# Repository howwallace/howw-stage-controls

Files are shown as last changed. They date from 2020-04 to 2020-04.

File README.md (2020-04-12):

# howw-stage-controls

AUTHOR:		Harper O. W. Wallace  
DATE:		12 Apr 2020

#### DESCRIPTION OF STAGES SETUP:

This library executes move commands for Zaber Technologies rotary (1 x X-RSW60A) and linear (2 x T-LSM050A) stages, all using binary encoding, and it supervises voltage and current control of Keithley 2400 SourceMeter to open and close a Thorlabs SH05 beam shutter.

The two linear stages are mounted in the plane of the ground (one atop the other) and oriented orthogonally such that, from the perspective of the upper stage's platform, one stage controls the "x-coordinate of position," and the other controls the "y-coordinate." Film samples prepared on 1-inch microscope slides can be mounted on the upper stage using a 3D-printed slide-holder (slide_holder.stl) that I designed to be compatible with Zaber T-LSM050A stages.

The upper stage's platform has a range of motion such that the laser beam emitted from a 671nm, 450mW Laserglow laser module can strike any point in much of the central area of the upper platform, and therefore any point on a mounted film sample. The beam is projected horizontally above the stages, strikes a mirror and reflects vertically down, and is focused through a 10x microscope objective; it can be interrupted programmatically by means of a Thorlabs SH05 beam shutter (mounted between source and mirror), which is operated by modulating current from the Keithley 2400 SourceMeter (cf. keithley_handler.py). The 10x microscope objective is suspended in the beam path (vertically; after reflection) and above the film sample, in the optic holder of a modified student microscope whose coarse control is connected to the rotary stage to allow for programmatic control of the distance between lens and sample (corresponds to "z" in execute_commands.py).

"Writing" (used below and in .py files) entails moving a thin film of thermoresponsive materials (donor-acceptor columnar liquid crystals) on the stages beneath the focused beam to control their columnar alignment. For this particular application, particular considerations must be made to speed, power, and focal distance, but for the purposes of this overview, it is sufficient to say that the path that the beam follows corresponds to the pattern written to the sample.

___

#### execute_commands.py:

Parametrized move commands allow the user to write a single line, write parallel lines, write part of a circle, write a full circle, wipe a region, outline a region, and home all stages merely by specifying relevant parameters (e.g., circle center, radius, and write speed); many of these write functions are parametrized in several different ways in order to simplify writing slight variations on the same type of pattern (e.g., horizontal lines that span the entire sample region, v. vertical lines that span a specified sub-region, v. diagonal lines that are separated by a specified perpendicular distance). These commands and their arguments are detailed in execute_commands.py.

#### coordinates.py:

A Cartesian coordinate system keeps track of sample boundaries and write command positions within them. This system confers particular advantages in allowing the user to keep track of previously-written and new patterns in a systematic way, and also in conserving area on sample films in order to maximize their usefulness between wipes.

The coordinate system is defined by two critical parameters (1–2) and one very helpful one (3):
1. **GLOBAL_O** (*V2*) = "global origin," or the x- and y- stage positions when the laser beam is focused on the bottom-left corner of a square sample film
2. **TR** (*V2*) = "top right," etc.
3. **LOCAL_O** (*V2*) = "local origin," effectively a pointer vector from the origin, which allows the coordinate system to be sub-defined for a given write command, without needing to redefine GLOBAL_O or TR.

Although GLOBAL_O stands for "global origin," TR is actually another global origin and is often the more critical of the two to determine accurately, since it is ends up defining the apparent "bottom left" origin position relative to which moves are made, once the coordinate system is inverted to account for inversion on viewing under a microscope.

The user can define values for GLOBAL_O and TR using POSITION_GETTER_MODE (in execute_commands.py), which allows her to take manual control of the stages (using control knobs on the stages themselves) to adjust their position until they reach a desired position on the sample (e.g., GLOBAL_O or TR). At this point, the user can press the 'p' key on the keyboard to print the position of the stages to the console, so they may be recorded, e.g., to define GLOBAL_O and TR for a new sample (press 'esc' once these values have been recorded).

Units are millimeters, but neither class of Zaber stages uses this unit explicitly; instead, they use microsteps (which I call "data" in conversion methods, because those values are what ends up getting sent to the devices). Conversion factors between distance and speed are not intuitive, and they are different for the rotary and linear stages. Understanding how these units are interconverted is key to resolving issues where the stages do not behave as expected, which can happen. Consult [1] for a detailed explanation of Zaber's units and conversions.

This coordinate system will be more useful if it is specified for EACH film sample. To facilitate maintaining these boundary positions for different samples, I have designed (and installed, in our setup in Ebaugh Labs at Denison University) a 3D-printable 1-inch glass microscope slide holder that can be mounted to the Zaber T-LSM050A stage so that this coordinate system is approximately (~0.01mm) conserved on removal and replacement of the sample (cf. slide_holder.stl). Values for GLOBAL_O and TR should be stored in sample-specific .txt files (cf. samples/_example.txt), which are read by execute_commands.py 

#### mapping_handler.py

A new and experimental feature of this library is move mapping, which theoretically allows the user to simulate how write commands will turn out in order to correct any errors before running them on a sample; as a sort of extension of the coordinate system itself, this feature too is meant to help conserve space on the film and maximize usefulness between writes. Move mapping will be particularly advantageous for writing multi-step patterns that will be necessary to generate complex diffraction gratings for Fourier projection and holographic images. As I explain in more detail in the header of mapping_handler.py, rendering hasn't been rigorously tested yet; but it verifying predicted paths for different commands should be straightforward, and a procedure is outlined in the header of mapping_handler.py.

mapping_handler.py consults the .txt data file corresponding to the relevant film sample to gather historical write data and defined global origins. These film sample files must be made available for each sample (at the path specified in execute_commands.py), and in the format specified in samples/_example.txt and samples/_template.txt. Notes on how film sample files are used are offered in execute_commands.py, but here are some notes on syntax:
- Film sample files are interpreted in such a way that is compatible with the actual Python syntax for calling these commands. This allows the user to copy and paste commands between sample .txt files and the manual command-calling section of execute_commands.py (rather than having to reformat from some other input format). It makes using Move Mapping much more convenient (if only because you have to be familiar with only one command-calling syntax), but you should note that parsing out varied-type (e.g., int, float, V2, arrays) arguments from a string in a text file is nontrivial: it is critical that you use exactly the format that I describe in samples/_template.txt, and even so it is also possible that there are some text-parsing bugs that you will need to resolve.
- The interpreter will respect Python-syntax line comments (i.e., "# ..."), so I'd recommend commenting in information about laser power so you can keep track of it.
- Film sample data files use a special symbol ("## ...") to mark section divisions between already-written commands, new commands, and references; this symbol should not appear elsewhere than those three places (cf. samples/_template.txt).

Limitations of mapping_handler.py:
- If you want to modify a command method (e.g., write_line(...)), then you'll have to make sure that the corresponding section in mapping_handler.py is updated; if you want to add a new command method, then you'll need to define one in mapping_handler.py for it to be rendered.
- It assumes that your frame of reference for writing is based on the image on viewing under a microscope, which is an inversion of how patterns are actually written to the sample (i.e., assumes INVERT = True, cf. execute_commands.py). This means that if you change the value of INVERT in execute_commands.py, then the preview rendered by mapping_handler.py will be inverted.
- It hasn't been designed to shift shift historical information if you redefine a sample's GLOBAL_O or TR.

___

#### EXTREMELY IMPORTANT NOTES:
1. **DO NOT LET THE OBJECTIVE LENS HIT THE SAMPLE HOLDER SCREWS:**
Although it is possible to programmatically set a minimum height for the rotary stage to alleviate concerns like this, unfortunately the screws are sufficiently elevated above the sample that the focal distance would probably be too large to write at modest power, if you were to try that (rather than doing it that way, I have set the minimum position such that the aluminum jacket for the objective lens will not collide with the screws, so that the linear stages should not be damaged in a collision). Therefore it is EXTREMELY IMPORTANT that you move the stages such that the objective lens is someplace within the sample region, THEN lower the objective lens to the correct focal distance. This is done automatically in the parametrized move commands defined below, but if you define any more, or if you call move_to(...), then you must consider stage height.

2. **DO NOT MELT THE BEAM SHUTTER BY LEAVING THE LASER BEAM ON IT TOO LONG:**
If the laser spot is on the shutter leaves for too long, they will deform and the diaphragm will no longer be able to open and close. For the ThorLabs SH05 beam shutter we are using, about ten seconds is safe given the wavelength, spot size, and highest throughput of our laser (according to a ThorLabs Application Technician). This can be an inconvenience when you would like to move around the sample film without dragging an isotropic line behind you, e.g., and so it means that you may have to find creative ways to organize writing to minimize the time that the laser needs to be effectively "off"; alternatively, you may find that raising the objective lens sufficiently high will diffuse the beam such that you can move the sample without aligning/disaligning; as a last resort, you may need to TURN THE LASER OFF MANUALLY in certain circumstances, rather than relying on the beam shutter.

3. **DO NOT MOVE THE ROTARY STAGE AT TOO GREAT A SPEED OR ACCELERATION:**
Stage accelerations are defined in execute_commands.py (define_operating_constants), and I strongly recommend that you not alter them. The primary reason that you should not increase the rotary stage acceleration is that it'd be a huge problem if you bent or snapped the pin that runs through the coarse control of the microscope stage and which the rotary stage is rotating to control stage height; if this pin twists too abruptly (and I have no idea what the damage threshold is), you're probably going to need to build a new z-control stage and a new control adapter for the rotary stage, and you may do direct damage to the rotary stage and/or the object lens.
It's also important not to let the rotary stage move too fast: though it is possible with the linear stages, incorrect moves of the rotary stage are much more likely to cause actual damage (to the objective lens, to the sample, to the linear stages, and to itself). I've set an upper bound on speed so that the rotary stage moves slowly; this allows you to manually stop it (by pressing in once on the manual control knob) if it looks like it's heading for dangerous territory.

4. **YOU CAN INTERRUPT PROGRAMMED STAGE MOVES BY PRESSING SHIFT-CTRL-C**
I strongly recommend playing around with sending commands and interrupting them with Shift-Ctrl-C so you know. One notable quirk is that, if you interrupt writing a circle, the most recent move_vel command stands, and so one or both of the linear stages may just keep going until it is fully extended; obviously, this is a big concern if the tip of the objective lens is below the level of the sample holder screws.

5. **PUTTING A Nd MAGNET ARRAY DIRECTLY ON THE LINEAR STAGES INTERFERES WITH THEIR OPERATION**
They sort of spazzed out there, for a while. If you are interested in aligning in a strong B field, then make sure that you have the magnet array sufficiently far away from the stages (e.g., mounted above, with a several-inch spacer).

#### TROUBLESHOOTING:
- In Zaber Console, if pressing the "Stop" button does not update a stage's current position, it's probably because disable_auto_reply (used in binarydevice.py to selectively silence/allow responses) is still on. Still in Console, click on the device, then Settings, and reset "Device Mode" such that bit 0 = 0 (i.e., round down to the nearest even number).
- ModuleNotFoundError probably means that it has not been installed. Instructions for installing pip: https://pip.pypa.io/en/stable/installing/. Once it's installed, call: [sudo] pip install [the name of the module].
- You must multiple V2 objects by integers, rather than integers by V2 objects (cf. note in coordinates.py).
- If you turn the manual control knob on the rotary stage and it doesn't move, it's in Displacement Mode. To put it back in Velocity Mode, push in the control knob and hold it for a few seconds until the light blinks.
- If a serial connection cannot be made to the stages, make sure you've plugged in the USB to the port specified in execute_commands.py (define_operating_constants), or change the specified port to match where it's actually plugged in.

#### NOTES ON VERSION HISTORY
- Older versions of these Python libraries are available in this repo, but unfortunately they weren't saved as meaningful commits (i.e., I didn't use GitHub) but rather as ~random snapshots from when I got nervous about not having multiple copies. You may find it helpful to consult these versions to resolve issues, but note that I can't guarantee that the older versions were saved in fully functional states (e.g., maybe I was in the middle of adding new functionality when I saved them, I just can't remember, and now I can't test them).
- Control over Zaber stages alone is possible using old C# scripts (also available in this repo) that work with Zaber Console. Those files obviously have very different syntax, but more importantly they interact with Zaber stages quite differently; they may still be useful, though.

#### REFERENCE:
[1] https://www.zaber.com/protocol-manual?protocol=Binary  
[2] https://www.zaber.com/support/docs/api/core-python/0.9/binary.html#binary-module

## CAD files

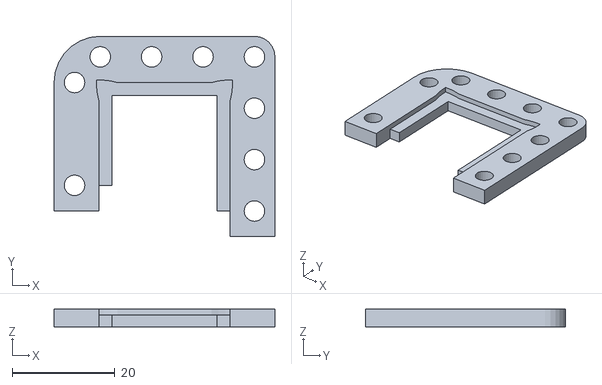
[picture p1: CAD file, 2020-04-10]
slide_holder.stl
43.0 x 39.0 x 3.50

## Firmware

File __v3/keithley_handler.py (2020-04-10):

#!/usr/bin/env python
# -*- coding: utf-8 -*-

import time
import visa
import numpy as np

"""
The keithley object that will manage the transmission of data and commands.

author: T. Max Roberts
"""

class Keithley:
    
    def __init__(self, addr = 24):
        try:
            rm = visa.ResourceManager()
            self.keith = rm.open_resource('GPIB0::%i::INSTR' %(addr))        
            self.run_start_up_commands()           
        except:
            print("Something went wrong...")
            sys.exit(0)
        
    def run_start_up_commands(self):
        for com in start_up_commands:
            self.send_command(com)
            time.sleep(.01)

    def send_command(self, command):
        response = self.keith.write(command)
        if response != '':
            return response
        else:
            return None
        
    """   all the useful commands as methods   """

    def reset(self):
        self.send_command('*RST')

    def set_output_on(self):
        self.send_command(':OUTP ON')

    def set_output_off(self):
        self.send_command(':OUTP OFF')

    def set_source_type(self, source_type):
        source_type = source_type.lower()
        if source_type == 'current' or source_type == 'curr' or source_type == 'c':
            self.send_command(':SOUR:FUNC CURRENT')
        elif source_type == 'voltage' or source_type == 'volt' or source_type == 'v':
            self.send_command(':SOUR:FUNC VOLT')
        else:
            print("Unknown source setting!")

    def set_source_voltage(self, voltage):
        if type(voltage) == int or type(voltage) == float:
            if voltage > 200:
                voltage = 200
                print("Voltage limits are  +/- 200 V")
            if voltage < -200:
                voltage = -200
                print("Voltage limits are  +/- 200 V")
            self.set_source_type('voltage')
            self.send_command(':SOUR:VOLT %s' %voltage)
        else:
            print("Bad voltage sent")

    def set_source_current(self, current):
        if type(current) == int or type(current) == float:
            if current > 1:
                current = 1
                print("Current limits are  +/- 1 A")
            if current < -1:
                current = -1
                print("Current limits are  +/- 1 A")
            self.set_source_type('current')
            self.send_command(':SOUR:CURR %s' %current)
        else:
            print("Bad current sent")

    def set_sensor_type(self, sensor_type):
        sensor_type = sensor_type.lower()
        if sensor_type == 'current' or sensor_type == 'curr' or sensor_type == 'c':
            self.send_command(':SENS:FUNC "CURR"')
            return 'current'
        elif sensor_type == 'voltage' or sensor_type == 'volt' or sensor_type == 'v':
            self.send_command(':SENS:FUNC "VOLT"')
            return 'voltage'
        else:
            print("Unknown sensor setting!")
            return None

    def set_sensor_range(self, sensor_type, sensor_range):
        sensor_type = self.set_sensor_type(sensor_type)
        print("Sensor type set to %s" %sensor_type)
        if type(sensor_range) == int or type(sensor_range) == float:
            order = int(('%.2E' %sensor_range)[5:])
            if sensor_type == 'voltage':
                self.send_command(':SENS:VOLT:RANG 10E%s' %order)
            elif sensor_type == 'current':
                self.send_command(':SENS:CURR:RANG 10E%s' %order)
            else:
                print("Shouldn't get here!")
        else:
            print("Bad range sent.")

    def set_voltage_compliance(self, limit):
        if type(limit) == int or type(limit) == float:
            coeff = float(('%.2E' %limit)[:3])
            order = int(('%.2E' %limit)[5:])
            self.send_command(':SENS:VOLT:PROT %sE%s' %(coeff, order))
        else:
            print("Bad compliance value sent.")

    def set_current_compliance(self, limit):
        if type(limit) == int or type(limit) == float:
            coeff = float(('%.2E' %limit)[:3])
            order = int(('%.2E' %limit)[5:])
            self.send_command(':SENS:CURR:PROT %sE%s' %(coeff, order))
        else:
            print("Bad compliance value sent.")

    def set_num_triggers(self, num):
        if type(num) == int:
            if num < 1:
                print("Number of triggers must be between 1-2500")
                print("Triggers set to 1")
                num = 1
            if num > 2500:
                print("Number of triggers must be between 1-2500")
                print("Triggers set to 2500")
                num = 2500
            self.send_command(':TRIG:COUN %s' %num)
        else:
            print("Bad trigger value sent.")

    def get_num_triggers(self):
        response = self.get_response(':TRIG:COUN?')
        return int(response.replace(' ', ''))

    def read(self, data_type=None):
        if data_type == None:
            self.send_command(':FORM:ELEM TIME, VOLT, CURR, RES')
        elif data_type.lower() == 'v':
            self.send_command(':FORM:ELEM TIME, VOLT')
        elif data_type.lower() == 'c':
            self.send_command(':FORM:ELEM TIME, CURR')
        elif data_type.lower() == 'r':
            self.send_command(':FORM:ELEM TIME, RES')
        else:
            self.send_command(':FORM:ELEM TIME, VOLT, CURR, RES')
        self.send_command(':OUTP ON')
        time.sleep(.25)
        self.send_command(':INIT')
        time.sleep(.25)
        # FETCH? waits for INIT to complete
        response = self.get_response(':FETCH?')
        time.sleep(.25)
        self.send_command(':OUTP OFF')
        return parse_data(response, data_type=data_type)

    """
    # delay = pulse time at each current;  rel_gap_delay = relative length of gap between pulses
    #   (e.g., 0.25 = 1/4 gap per 1 pulse => 0.2 : 0.8 = gap : pulse)
    def current_sweep(self, start, stop, step=0.02, delay=0.1, rel_gap_delay=0.25):
        
        if gap_delay == 0:
            sweep_list = range(start, stop + step, step)
        else:
            sweep_list =
        # ...
        
        trig_count = (stop-start)/step + 1
        self.send_command('*RST')                   # restore GPIB default conditions
        self.send_command(':SENS:FUNC:CONC OFF')    # turn off current configurations
        self.send_command(':SOUR:FUNC CURR')        # current source
        self.send_command(":SENS:FUNC 'VOLT'")      # monitor voltage
        self.send_command(':SENS:VOLT:PROT 7.5')    # set 7.5V voltage compliance
        self.send_command('SOUR:CURR:MODE LIST')    # list current sweep mode
        self.send_command('SOUR:LIST:CURR %s' %(sweep_list))        # list current sweep mode
        self.send_command(':TRIG:COUNT %i' %(count(sweep_list)))    # set sweep points
        self.send_command(':SOUR:DEL %f' %(adj_delay))              # set source delay
        self.send_command(':OUTP ON')               # turn on source output
        self.send_command(':READ?')                 # trigger sweep, request data
    """

    """
    def sweep(self, data_type=None, start=-10, stop=10, step=1, delay=0.1, num_sweeps=1):
        sweep_points = (stop-start)/step + 1
        num_trigs = num_sweeps*sweep_points
        if data_type == None:
            self.send_command(':FORM:ELEM TIME, VOLT, CURR, RES')
        elif data_type.lower() == 'v':
            self.send_command(':FORM:ELEM TIME, VOLT')
        elif data_type.lower() == 'c':
            self.send_command(':FORM:ELEM TIME, CURR')
        elif data_type.lower() == 'r':
            self.send_command(':FORM:ELEM TIME, RES')
        else:
            self.send_command(':FORM:ELEM TIME, VOLT, CURR, RES')
        self.send_command(':SOUR:FUNC VOLT')
        time.sleep(delay)
        self.send_command(":SENS:FUNC 'CURR:DC'")
        time.sleep(delay)
        self.send_command(':SENS:CURR:PROT 0.5')
        time.sleep(delay)
        self.send_command(':SOUR:VOLT:START %s' %start)
        time.sleep(delay)
        self.send_command(':SOUR:VOLT:STOP %s' %stop)
        time.sleep(delay)
        self.send_command(':SOUR:VOLT:STEP %s' %step)
        time.sleep(delay)
        self.send_command(':SOUR:VOLT:MODE SWE')
        time.sleep(delay)
        self.send_command(':SOUR:SWE:RANG AUTO')
        time.sleep(delay)
        self.send_command(':SOUR:SWE:SPAC LIN')
        time.sleep(delay)
        self.send_command(':SOUR:SWE:POIN %s' %sweep_points)
        time.sleep(delay)
        self.send_command(':TRIG:COUN %s' %num_trigs)
        time.sleep(delay)
        self.send_command(':SOUR:DEL 0.1')
        time.sleep(delay)
        self.send_command(':OUTP ON')
        time.sleep(delay)
        self.send_command(':INIT')
        # FETCH? waits for INIT to complete
        response = self.get_response(':FETCH?')
        time.sleep(.25)
        self.send_command(':OUTP OFF')
        return parse_data(response, data_type=data_type)
    """


"""
This function parses the data returned from the Keithley.
The data is stuctured as {Volts, Amps, Ohms, Timestamp, Status}.
This creates an array of {Time, Volts, Amps, Ohms}.
Each element is a column vector for easy plotting.
KEYWORDS:
data_type = 'v' returns only time and volts, 'c', only time and current,
'r' only time and ohms.
"""
def parse_data(data, data_type=None):
    # Clean up the strings, splits into list
    data = data.replace(' ', '').split(',')
    # Reshape in sections
    if data_type in ['v', 'c', 'r']:
        cols = 2
    else:
        cols = 4
    # NOTE If data is not returned in groups of "cols" this will drop elements!
    data = zip(*[iter(data)]*cols)
    # Use an array as they can be indexed, and for type conversion
    data = np.array(data).astype(np.float)
    if data_type == None:
        return np.array([data[:,3], data[:,0], data[:,1], data[:,2]])
    elif data_type.lower() == 'v':
        return np.array([data[:,1], data[:,0]])
    elif data_type.lower() == 'c':
        return np.array([data[:,2], data[:,0]])
    elif data_type.lower() == 'r':
        return np.array([data[:,3], data[:,0]])
    else:
        print("Bad data_type given, returning full data set")
        return np.array([data[:,3], data[:,0], data[:,1], data[:,2]])

"""  Fast Settings  """
start_up_commands = ["*RST",
                     ":SYST:TIME:RES:AUTO 1",
                     ":SYST:BEEP:STAT 0",
                     ":SOUR:FUNC CURR",
                     ":SENS:FUNC:CONC OFF",
                     ":SENS:AVER:STAT OFF",
                     ":SENS:CURR:NPLC 0.01",
                     ":SENS:VOLT:NPLC 0.01",
                     ":SENS:RES:NPLC 0.01",
                     ":SENS:FUNC 'VOLT'",
                     ":SENS:VOLT:RANG 1e1",
                     ":TRIG:DEL 0.0",
                     ":SYST:AZER:STAT OFF",
                     ":SOUR:DELAY 0.0",
                     ":DISP:ENAB OFF"]

class FakeKeithley(object):
    def __init__(self):
        for method in Keithley.__dict__:
            self.__dict__[method] = self.fake_method
    def fake_method(self, *arg, **kwarg):
        pass
